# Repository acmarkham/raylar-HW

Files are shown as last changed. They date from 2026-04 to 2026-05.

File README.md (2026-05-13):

# raylar-HW
## Caracal Raylar Hardware Repo

This is the main repository for the bioacoustic platform Caracal Raylar. This is an updated version of the CARACAL EVO (2021) design, which itself is an evolution of SHUMBA (2019). The main features are:

- Six onboard microphones, low frequency rolloff 7Hz
- microSD card for storage
- Onboard GPS for precision timestamping and location
- Onboard dual band wireless (sub-GHz plus 2.4GHz) for mesh networking
- STM32U5 core, supports up to 3.5MB RAM depending on variant
- Multi-source power tree including
  - USB
  - Solar
  - Rechargeable single cell lipo
  - External battery 6V-12V
- Onboard accelerometer and magnetometer/compass for tilt and direction
- Extension connectors: 
  - QWIIC x 2 (easy to plug in peripherals like a OLED display) 
  - Mikrobus MBUS (supports a huge ecosystem of sensors)
  - EXT
  - DEBUG
- Beeper/LEDs for user feedback (errors, status etc)

## PCB

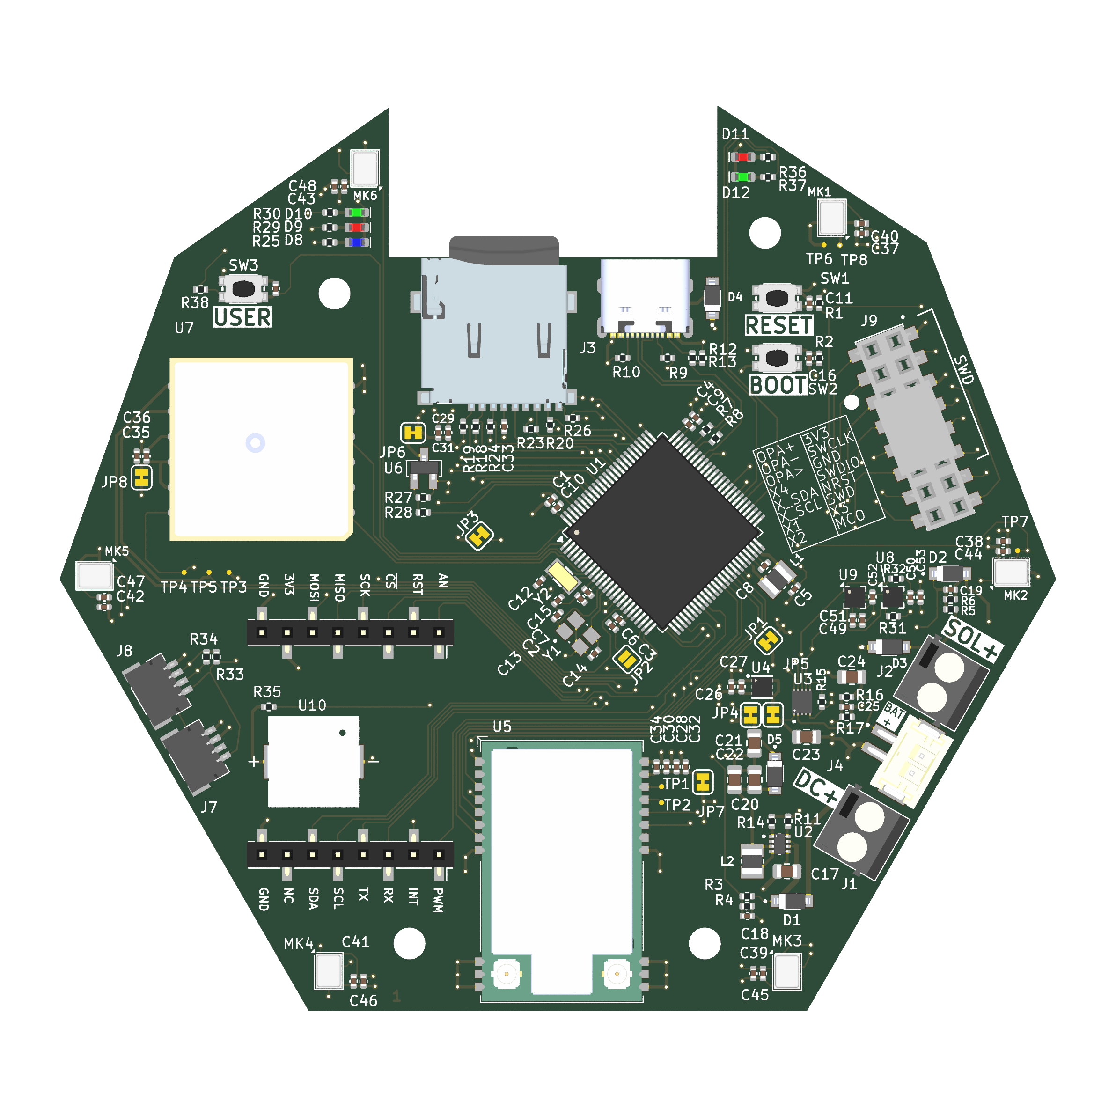
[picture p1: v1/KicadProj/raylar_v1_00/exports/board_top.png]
Top


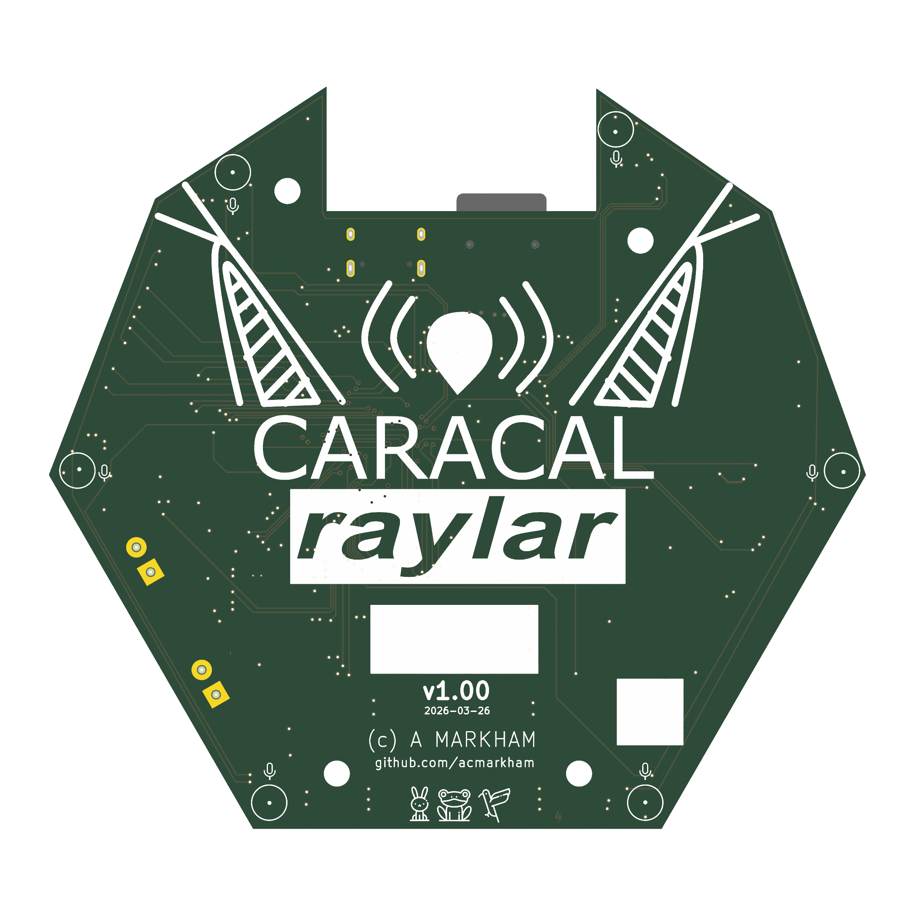
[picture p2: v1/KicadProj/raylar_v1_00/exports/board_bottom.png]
Bottom


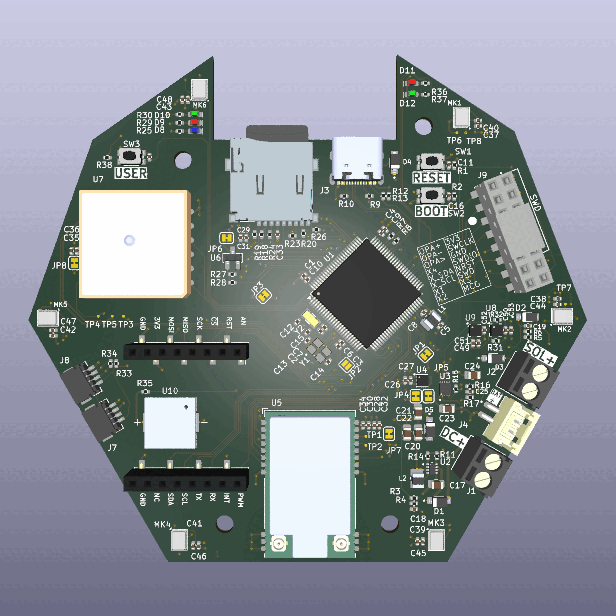
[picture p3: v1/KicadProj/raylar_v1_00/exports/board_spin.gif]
Render


## Schematic

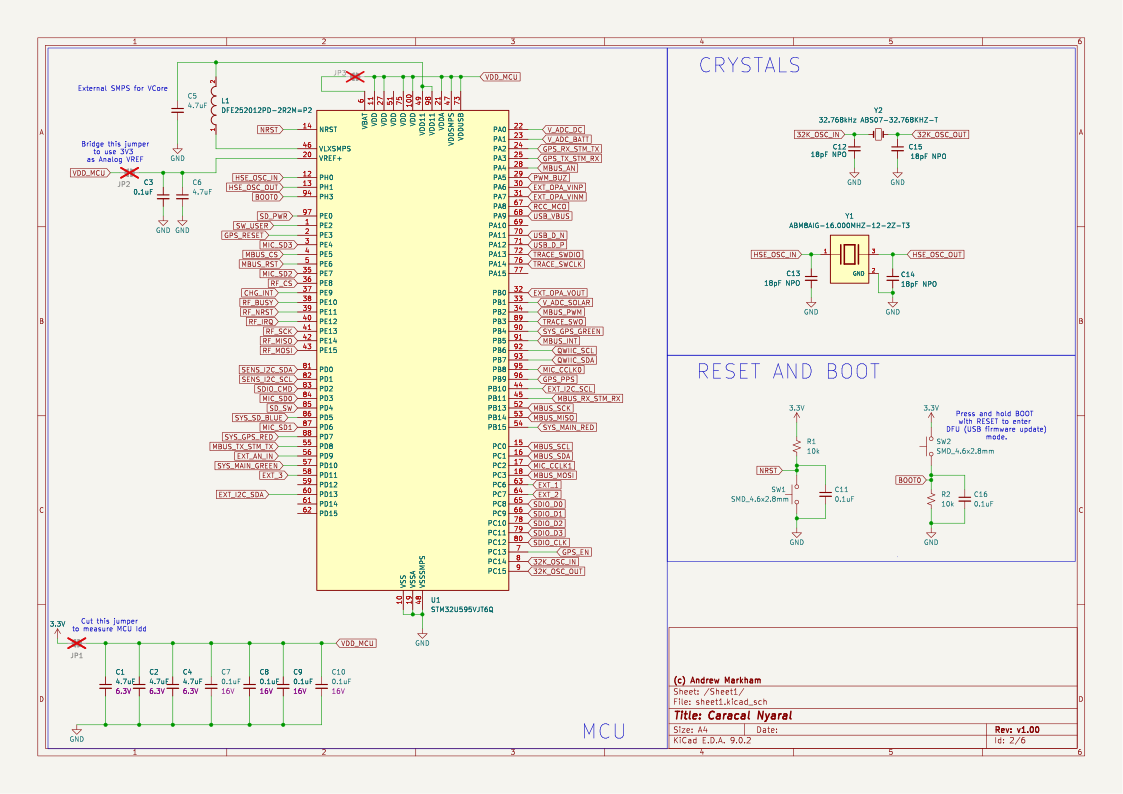
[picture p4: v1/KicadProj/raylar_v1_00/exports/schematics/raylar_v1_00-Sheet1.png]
Sheet 1 Schematic


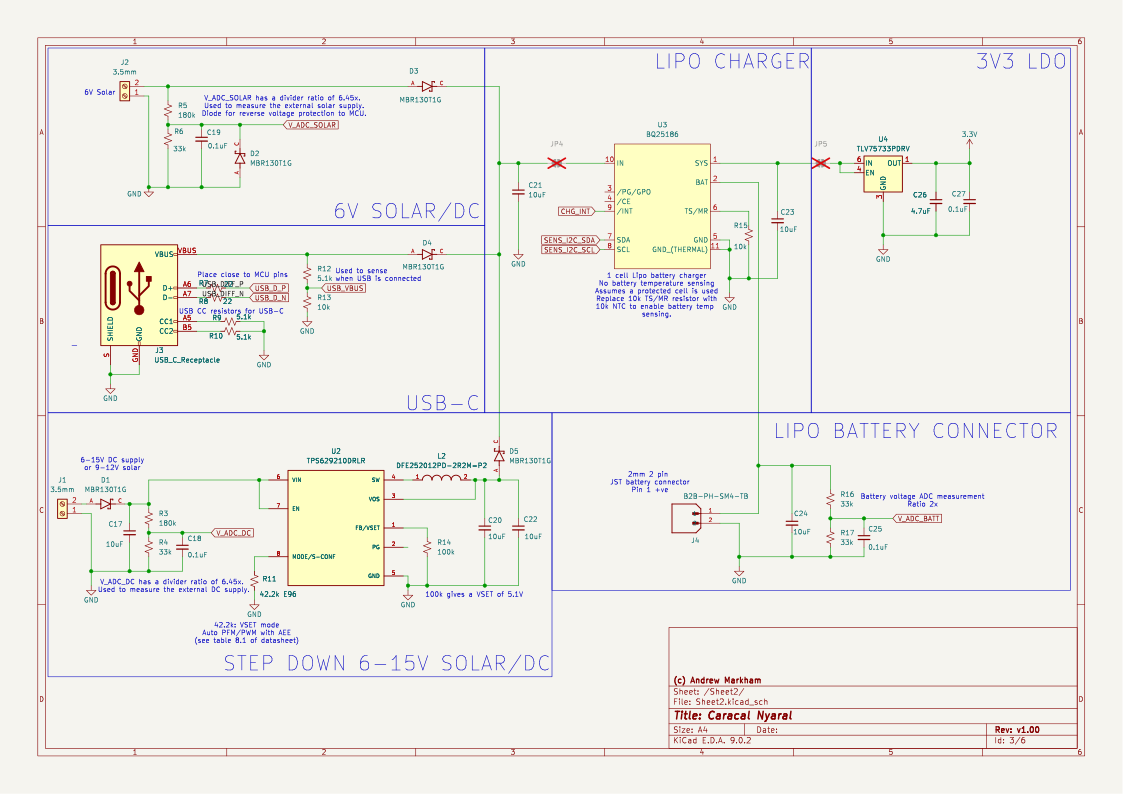
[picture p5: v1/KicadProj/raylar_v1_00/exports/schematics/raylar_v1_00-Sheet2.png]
Sheet 2 Schematic


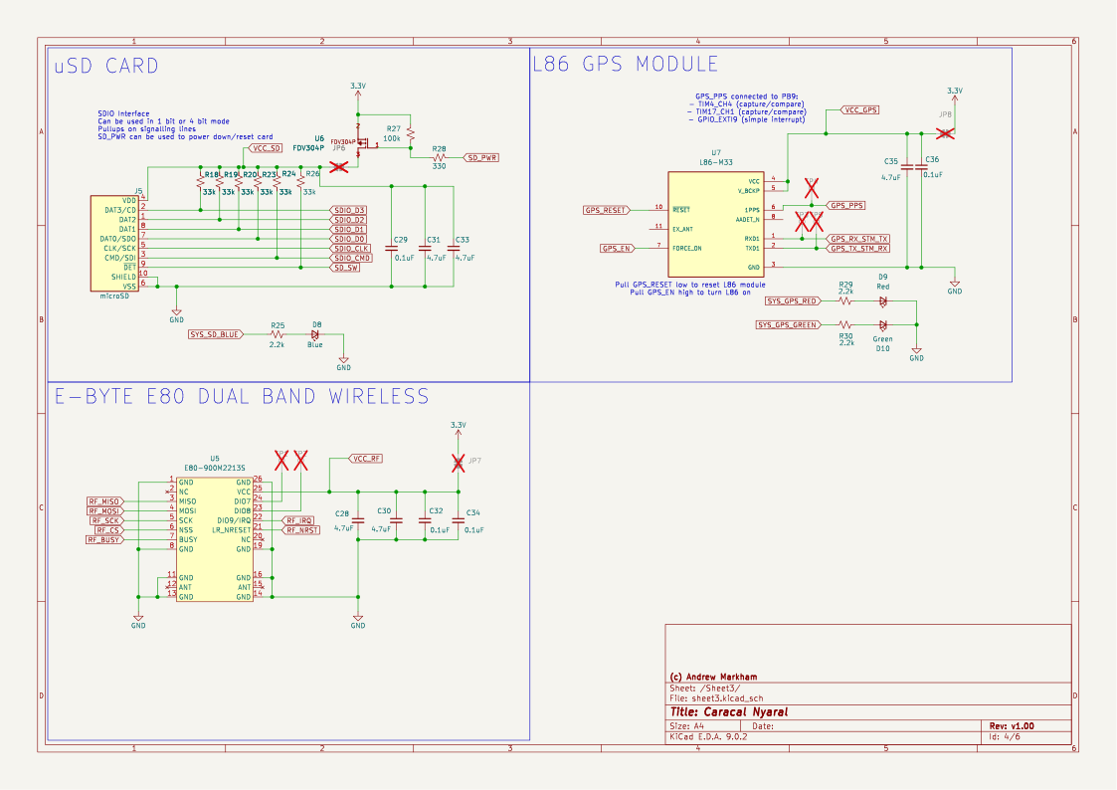
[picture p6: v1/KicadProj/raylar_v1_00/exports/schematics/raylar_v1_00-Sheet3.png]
Sheet 3 Schematic


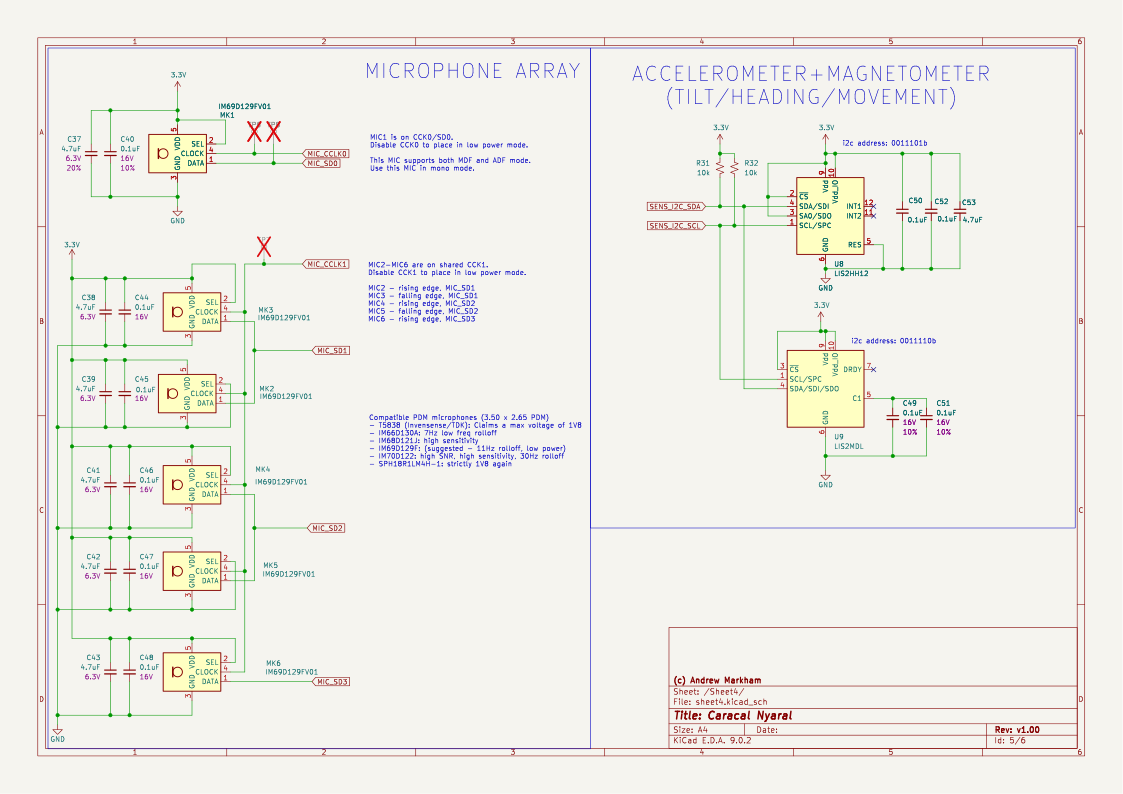
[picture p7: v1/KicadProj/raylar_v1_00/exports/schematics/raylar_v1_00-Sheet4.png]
Sheet 4 Schematic


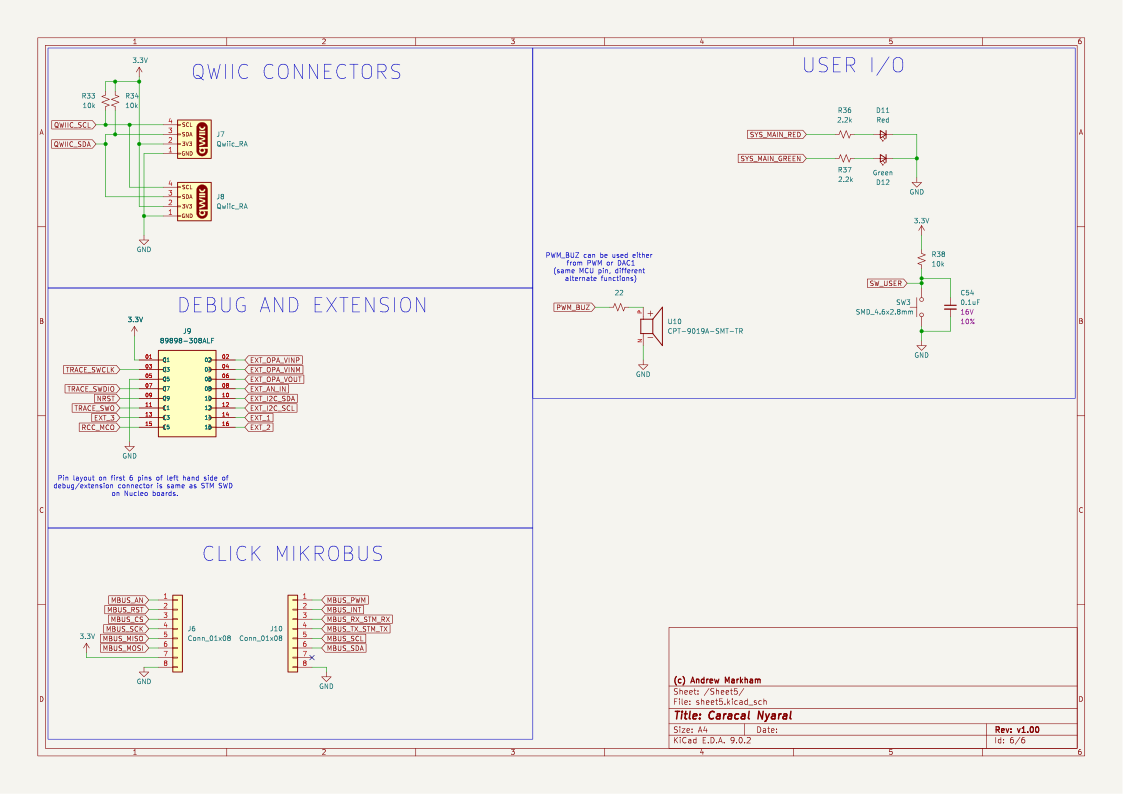
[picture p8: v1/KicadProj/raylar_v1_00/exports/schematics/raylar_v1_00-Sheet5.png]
Sheet 5 Schematic


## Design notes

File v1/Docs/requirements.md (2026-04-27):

# Caracal Raylar (formerly Nyaral) HW v1 Spec&Design

The previous variant of Caracal (Caracal EVO) had a number of features, specifically:

- 4-8 microphones, allowing for beamforming, DoA and stacking. Only 4 can be used at once because there are 4 DFDSM filters.
- GPS time synchronization, allowing TDOA and file timestamping
- SD card for long term storage
- STM32L4 micro (192kB RAM) which gave enough space for buffering
- Basic real-time processing (simple 1K NN, GCC-PHAT) if needed
- Dual source power (USB or 6-12V external battery)

For this version, the main requirements are:

* 6 microphones that can be used simultaneously (6 MDF filters)
* Lower power - previous version used around 40mA@3V when running at full tilt which is high
* Wireless connectivity - long range like LoRA as a minimum
* Onboard GPS
* Onboard tilt/direction/movement sensing
* Easy interface to additional sensors e.g. to MikroE Click or STEMMA QT
* Solar powered natively with USB or external
* Native support for LiPo 1C battery
* Voltage/charge measurement on inputs/battery
* Similar/lower price point (~$60 in 100 QTY)

Specific Requirements

- R1: STM32U5 family support (up to 4Mb RAM).
- R2: 6 high quality PDM microphones.
- R3: Wireless Interface (mesh).
- R4: GPS module
- R5: Tilt/compass sensor
- R6: Power module (solar + LDO/buck regulator). Dual input + battery charger.
- R7: microSD
- R8: Oscillator
- R9: Debug/program
- R10: User Interface
- R11: Extendability
- R12: Mesh gateway/listener
- R13: Mechanical

## Design Choices

### R1: STM32U5 family support (up to 4Mb RAM)

To be maximally compatible between wide varieties (i.e. RAM) of STM32, we will choose 100 pin LQFP package (existing caracal is 64 pin). We don't need to finalize now, but STM32U5G7VJT6 (3MB RAM $11/100) seems like a reasonable choice. Other pin compatible variants include:

* STM32U535VET6 [274k RAM] [$4.8/100]
* STM32U575VGT6 [768k RAM] [$5.0/100]
* STM32U585VIT6 [768k RAM] [$5.9/100]
* STM32U595VIT6 [2514k RAM] [$9.5/100]
* STM32U599VJT6 [2514K RAM] [$9.3/100]
* STM32U5A5VJT6 [2514K RAM] [$9.6/100]
* STM32U5A9VJT6 [2514K RAM] [$10.3/100]
* STM32U5F7VJT6 [3024K RAM] [$11.5/100]
* STM32U5F9VJT6 [3024K RAM] [$10.8/100]
* STM32U5G7VJT6 [3024K RAM] [$11.0/100]

This gives us a very neat upgrade/downgrade path e.g. to make a minimal caracal by stripping out more advanced features we can go for U575 and shave ~$5 off total BOM. For now, lets design for the max. There is also a question of package:

64 pin LQFP (previous caracal)

100 pin LQFP (reasonable "upgrade" path)

144 pin LQFP (might be a bit much, we don't have a screen or anything else that needs such a lot of GPIO)

144 pin UFBGA (could make design more complex, definitely need more than a double sided board).

Some of the smaller memory variants have 64 pin QFN which might be an option but not for the G7.

Note that there is also a -Q suffix which has a built in SMPS for the core. This can almost halve active power consumption e.g. at 160MHz run rate. It does sacrifice ~3 pins and potentially adds hash noise. But it is software enabled, so we can choose whether or not to use it in deployment.

> Choice: STM32U5G7VJT6Q (100 pin LQFP). This seems to be well supported for up/downgrade pathway.
>
> Alternatives: STM32U595VJT6Q (2.5M RAM, more widely available)

### R2: 6 high quality PDM microphones.

There are lots of variants here, we are looking for very high dynamic range and sensitivity, as well as a low frequency roll-off that will allow better infrasound. These are bottom port PDM microphones.

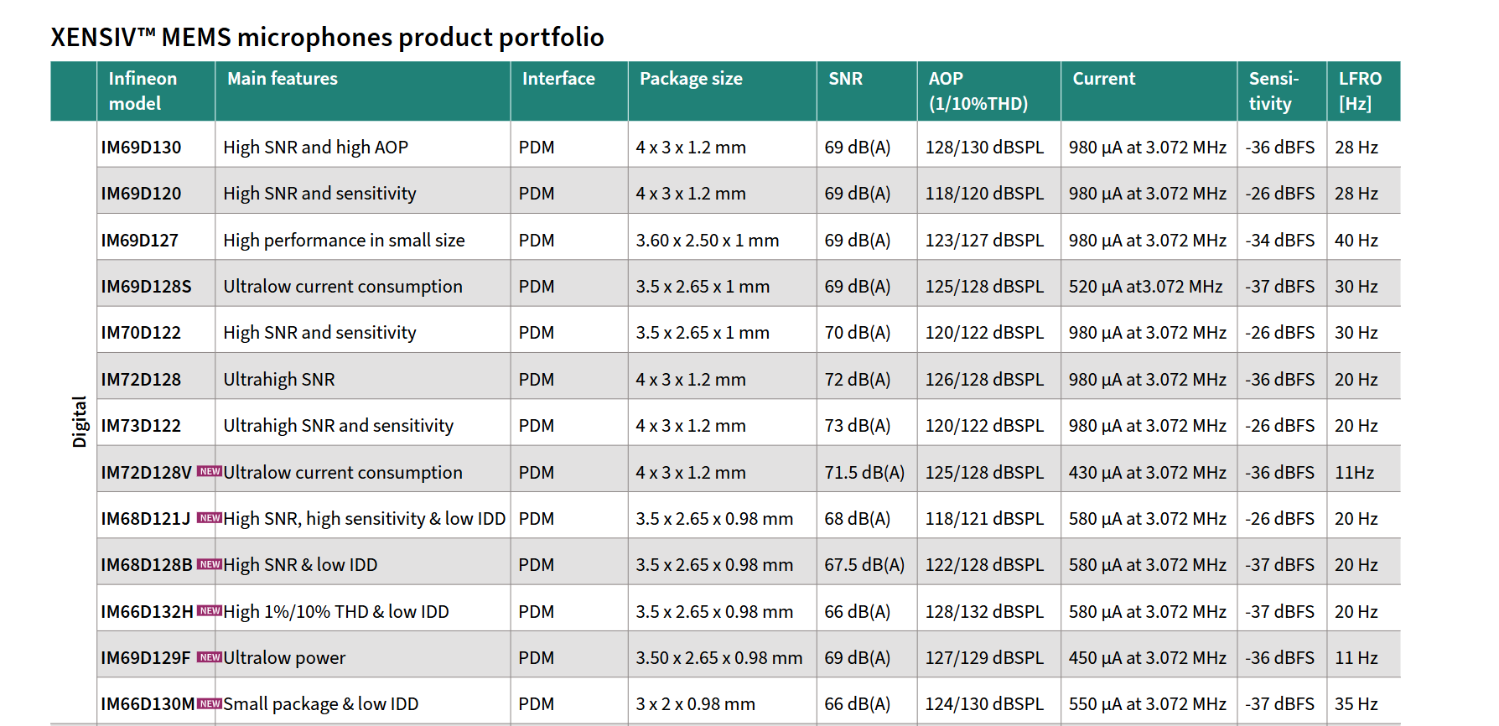
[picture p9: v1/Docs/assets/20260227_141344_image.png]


Pin compatible options include:

IM69D129F (infineon):

129dB SPL AoP, Sensitivity: -36dBFS, SNR: 69dB(A)

450uA, 11Hz LFRO.

Also, is IP57 rated which is a great feature.

3.50 x 2.65

T5838 (Invensense/TDK) [As used in the previous, second iteration of Caracal. Interestingly, it claims max supply voltage is 1V8, so it must have been unhappy).

133dB SPL AoP, Sensitivity: -41dBFS, SNR: 68dB(A)

310/120uA, 27HZ LFRO

3.50 x 2.65

Strictly, 1.8V max, which could be problematic

Others include Syntiant(Knowles)SPH18R1LM4H-1 [30Hz rolloff, 68dB(A)], (Infineon)IM66D130A [7Hz(!) rolloff, 66dB(A), 130dB AOP, 1100uA]

In a larger package (4x3) we have:

IM72D128V which has 71dB SNR.

> Choice: IM69D129FV01 (might be tricky to obtain as it is relatively new). Footprint is standard however, so many pin compatible options exist.

### R3: Wireless Interface (mesh)

This is challenging, as we want everything without having to pay for it ($BOM, footprint, power, opex). The base is LORA - this will allow easy compatibility and it is field proven to be long range. The next dimension to consider is DIY RF or solder down a module. Modules are more expensive, but are FCC/CA tested, so it reduces risk and does not need its own certification. They also are much lower risk in terms of impedance matching, board layout etc.

Main chipsets are SemTech and HopeRF.

SemTech LR1121 and LR2021 are dual band, which allows dense plus long-range meshing.

* Ebyte E80-900M2213S is LR1121 based ~ £5.80. Package is quite consistent across Ebyte modules. Widely available (even on Amazon). 26x16mm. Dual band. Antenna connector on module. Even supports L-band satellite uplink.
* Seeed studio Lora-E5-HF - based on STM32WLE5JCSTM3. Single band.
* RAK3172: Lora-E5-HF. Single band.
* Murata: LBAA0XV2GT-001 LR1121 based. ~£12.00. Dual band. Antennas are external traces, not on board, so that is a faff. But very small: 9.98 × 8.70mm. And probably more robustly designed than ebyte. Available at digikey. Compatible with different murata module, but will require different matching/front-ends.
* Core1121 (waveshare) ~$10ea. compatible with lots of different waveshares.
* Seeed Wio-LR1121 (IPEX4 1.5mm onboard). Does not seem to be available.
* LoRa1121 (NiceRF). Not neccesarily widely stocked/available.
* EMB-LR1121-e (Embit): EU company, no visible pricing

> Choice: EByte E80. But pull out the same pins for interfacing to a different module if needed. Consider dual footprint for alternative e.g. core1121 or RAK series as well to be safe?

### R4: GPS module

We have used ublox el-cheapos to date with varied results. Options are:

- External GPS + Antenna (connect via cable)
- Onboard GPS + External Antenna
- Onboard GPS + Onboard Antenna

External GPS + Antenna is the most flexible as we can chop and change antennas easily. But it is a nuisance because soldering is required by an end-user to add on the GPS. For 100 boards, this can easily take hours of time. I think we can safely discount this as a main option, but can easily have the GPS pins (power, serial RX/TX, EN, PPS) broken out anyway.

Onboard GPS + External antenna makes board config not a big issue as it doesn't really matter where the GPS is in terms of sky view/blocking. It also makes it simple to re-orient the board (horizontal/vertical) without heavily impacting skyview. It can be a risk in terms of antenna cables flapping around and falling off. This will be an issue anyway for the RF block, so it possibly is not a massive issue.

Combined GPS + antenna is super nice from a design perspective because a single "lump" just works.

- SAM-M8Q: (fully onboard). ublox GPS M8. Lovely, but expensive at ~$20/100
- SAM-M10Q: (fully onboard). ublox GPS M10. Amazing, but more expensive at $22/100
- Quectel LC86G: fully onboard. $8/100. Footprint compatible with L80 and L86 module.
- Quectel LC86L: fully onboard: £7/100. Compatible with Quectel GPS module L80.
- DAN-F10N-OOB: fully onboard. $15/100. dual band. ublox.

External antenna:

* max-f10s-oob: external antenna. $15/100.
* TESEO-LIV3 series 18LCC ~$10/100

External antenna options will be painful as they will need proper board routing. My bet is to go for Quectel series and then provide another GPS breakout to give max flexibility.

> Quectel LC86L. Secondary breakout for external GPS.

### R5: Tilt/compass sensor

Currently the device has to be manually surveyed in place which is painful. This is to ensure that MIC1 is facing north. An easier way is for the board to just "know" which direction it is facing. Conceptually easy, but compasses can have major hard-iron issues. Nonetheless, it should be better than the current approach. Adding a tilt sensor (accelerometer) will also allow for sensor to be placed at arbitrary tilts and then this info used. Tilt sensor can also be used for wakeup/theft/tampering detection.

* Bosch BNO055. 9 axis IMU. $9/100
* LIS2HH12TR (acc) + LIS2MDLTR (mag) - $0.6 + $1
* LIS3DHTR (acc) + LIS2MDLTR (mag) - $0.8 + $1
* Melexis: MLX90392ELQ-AAA-010-RE (mag) - $0.51
* LSM303AGR: eCompass - $2.55/ea (long lead times)
* ICM-20948: Full 9 axis IMU - $5

> Choice: LIS2HH12 (acc) + LIS2MDL (mag)

### R6: Power module (solar + LDO/buck regulator). Tri input + battery charger.

Here, we want to be able to flexibly power our modules from:

- A standard 1 cell rechargeable lipo (3v6), charged by USB/Solar
- USB
- Solar
- External VBAT (6-12V)

### Charger options

* bq25185: Very simple, minimal BOM $1.2/100. Diode OR for the multiple power sources. Also, without the battery, it just does a straight pass-through, so the battery is actually optional.
* BQ25186: Same as bq25185 but with i2c i/o. Newer, so might be harder to get hold of.
* bq24074: higher charge current, supports higher voltage panels $1.3/100
* BQ25895: i2c telemetry and control $2/100
* LT3652: MPTT $5/100

### 12V buck options

For a higher voltage input, we don't want a linear regulator as it will drop the excess voltage as heat. Instead, we use a buck which is more efficient.

TI **TPS62160** (3–17 V in, 1 A sync buck, high switching frequency)

TPS629210 (3-V to 17-V, 1-A, high-efficiency, low-IQ, synchronous buck converter in SOT-583 package)

### Fuel gauge:

* BQ27441 (and -G1 suffix): colomb counter $1.8/100
* BQ27532
* MAX17048: voltage shunt $2.2/100

### Voltage regulation

* We need to drop the SYS regulated voltage down to stable 3V3 (or perhaps lower? It is probably now only the microSD that wants a higher voltage...)
* We can buck-boost, boost-ldo or just LDO. LDO looks like the most straightforward...
* TPS72633
* MCP1700 series (170mV drop at 250mA), $0.4/100. Iq is 10uA
* MCP1824 series (300mA), $0.5/100. Iq is higher at 29uA typ.
* TLV75733: Full part number TLV75733PDRVR (1A), Iq is 25uA typ

https://e2e.ti.com/support/power-management-group/power-management/f/power-management-forum/1605244/bq25185-bq25185---simple-solar-charging-circuit?tisearch=e2e-sitesearch&keymatch=bq25185#:

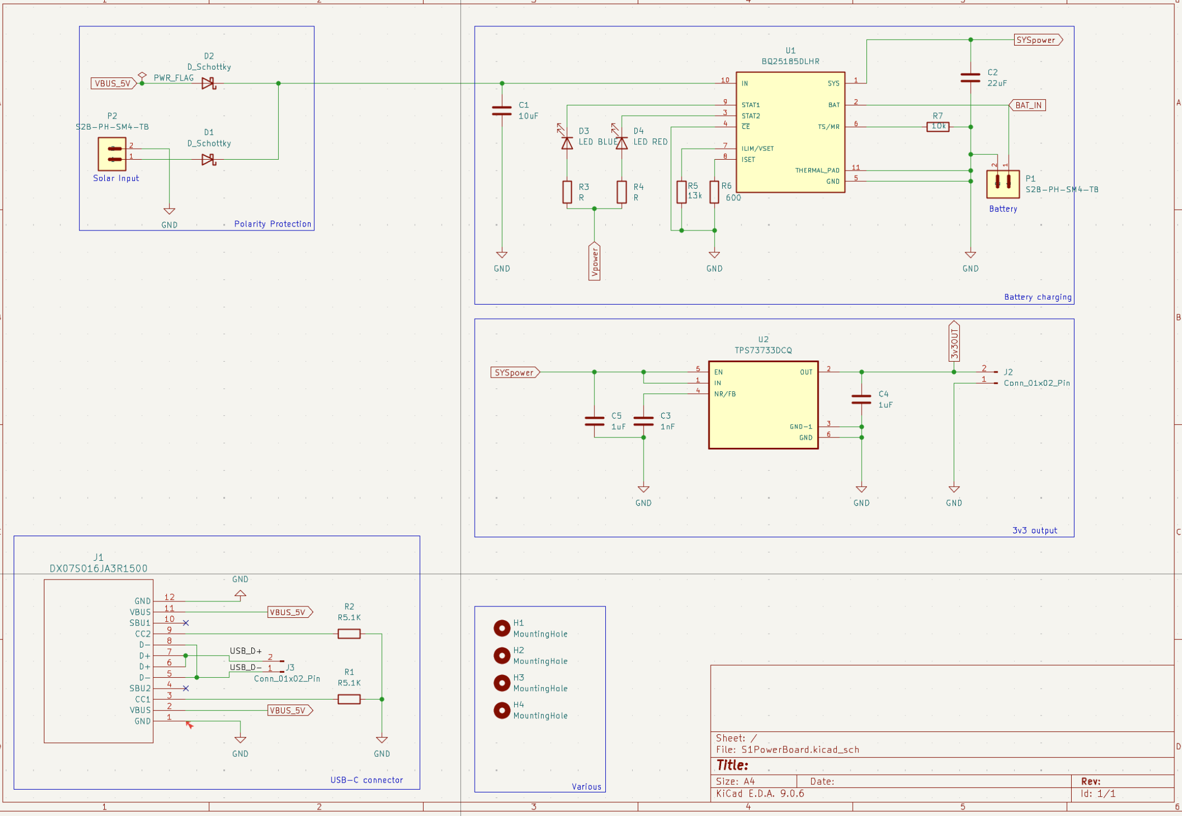
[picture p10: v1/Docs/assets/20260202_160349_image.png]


> Choice:
>
>> BQ25186 for battery charge and passthrough
>>
>
>> TPS629210 buck from external 6-12V down to 5V
>>
>
>> BQ27441 (optional) for colomb counting, can use MCU ADC for very rough estimate.
>>
>
>> MCP1824T-ADJE/OT for adjustable, stable 3V rail
>>

### R7: Microsd

We want to be able to use microsd in SDIO mode, but also to power it down. This is necessary for low power consumption and also sometimes needed for reset.

- Use 10k pullup on signalling lines (some use 33k or 47k)
- Use 22R to prevent high speed ringing (optional)
- 10uF X5R decoupling (at least)

Here is an example of low voltage (1v8) SDIO:

https://oshwlab.com/grafalex/low-voltage-sdio

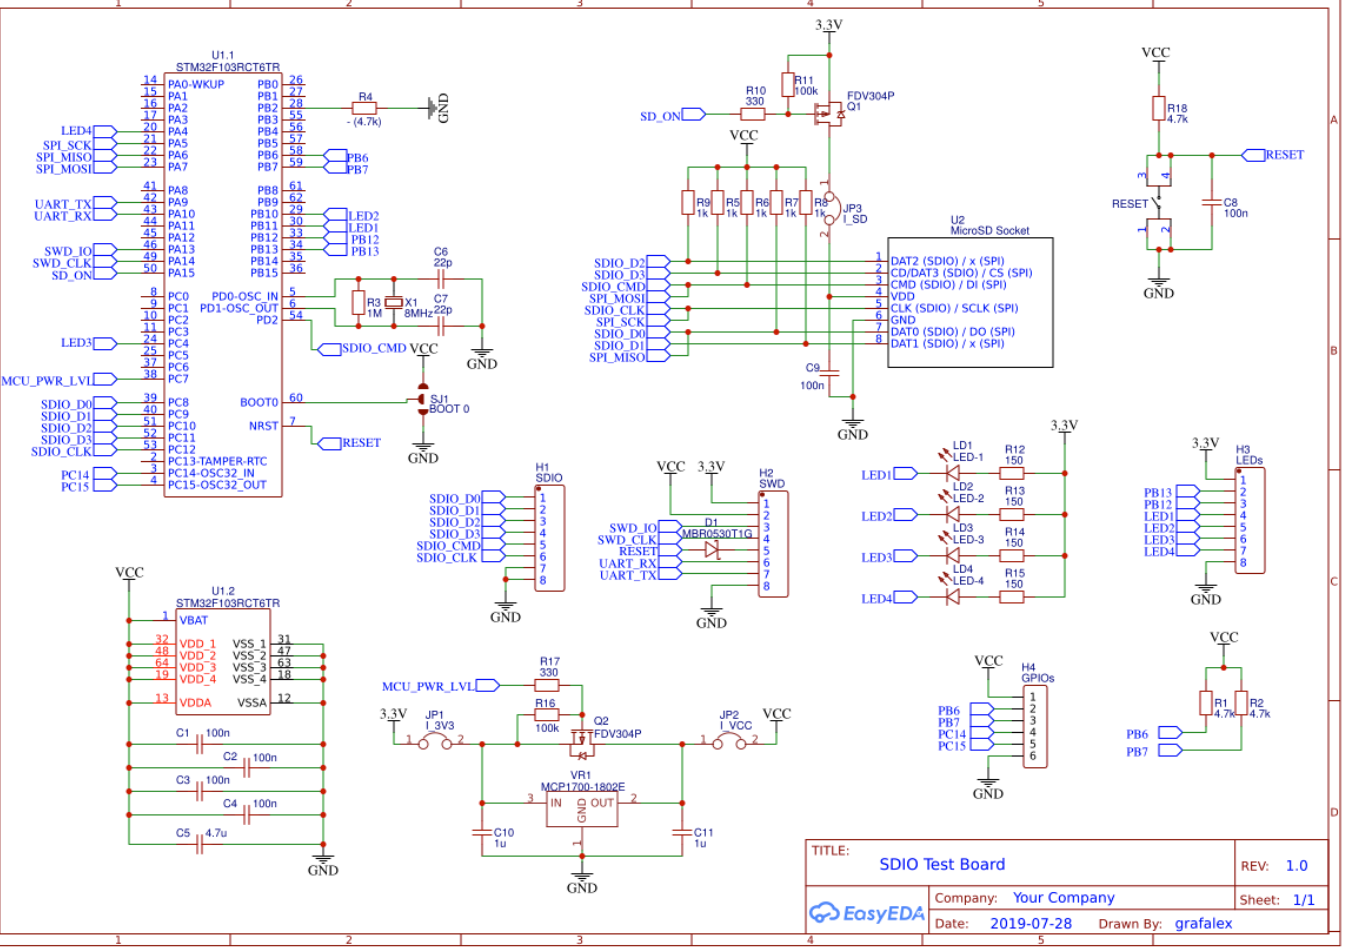
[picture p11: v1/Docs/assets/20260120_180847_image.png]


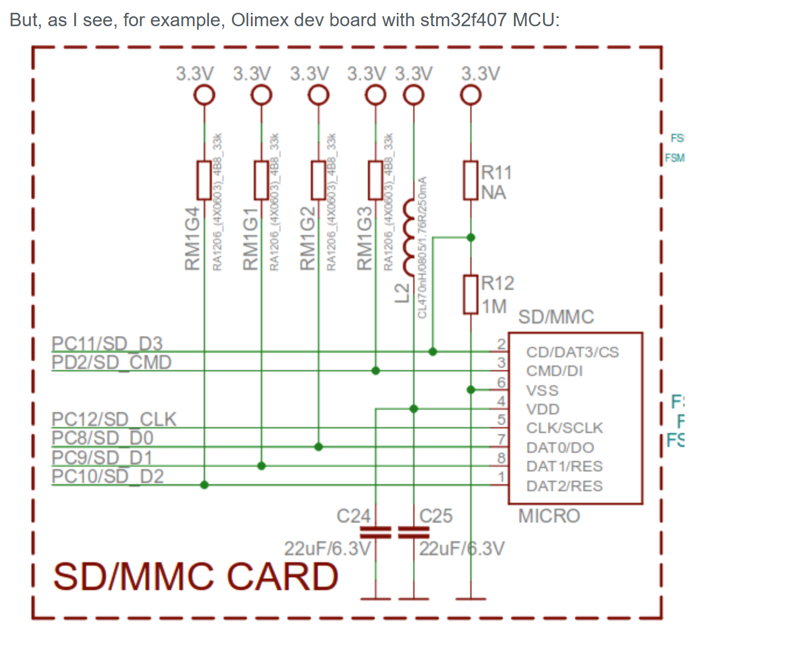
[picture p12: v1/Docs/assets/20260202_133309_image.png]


For power control:

- TPS22917: high side power control with inrush ($0.6/100)
- FDV304P: P-channel mosfet ($0.12/100)

> Choice: TPS22917. 10k pullups. No 22R ringing resistor. SD card presence switch. 10uF/100nF X5R decoupling. Push-push SD card.

### R8: Oscillator

We need a reasonable XO for HSE. In particular, for Caracal EVO, small drifts lead to files not having a "true" sampling rate e.g. of 16kHz. This especially will become more pronounced towards the end of the file as the epoch is synchronized at the beginning. This can lead to tens of milliseconds of sampling offset with a standard 20ppm XO. Although we use GPS to start each file on the top of the hour, we don't modify the actual sampling rate. STM32U5 has a nice feature (fractional PLL) which can provide finer grained frequency stepping. We can use GPS PPS to make a GPS disciplined oscillator to get below 1ppm sampling rate error.

* Abracon ASEMB-16.000MHZ-LY-T: Oscillator MEMS 16MHz ±10ppm (Stability) 15pF LVCMOS. $0.9/100. 10mA(!) current consumption.
* ABRACON ATX-H11-F-16.000MHz-G100-T: 10ppm MEMS, $1/100. 4.8mA current consumption
* SiT3907AC-2F-33NE-16.000000Y: 10ppm MEMS, limited supply, $8/100
* ABM10N-16.0000MHZ-8-D1X-T3: 10ppm XO, $0.5/100. Tiny package SMD4
* ABM8AIG-16.000MHZ-12-2Z-T3: 20ppm XO, $0.7/100. 3.2x2.5 standard package.

Do we need a 32kHz oscillator? These can allow for backup time/date without running HSE. I am not convinced this is necessary as power budget is largely dominated by RF and GPS, not so much idle. Also, when running PDM, it is most likely we will be clocked from HSE as we need PLL for MCO.

> Choice: ABM10 or ABM11 series if footprint works. ABM8 for more flexible variant.
>
> ~Choice: No 32kHz in this iteration~
> Actually, lets go for a 32kHz, AB07 series

### R9: Debug and program

For debug, the main options are to consider which connectors to use onboard. The simplest and cheapest is to just have solder/test pads and use a small set of boards as designated debug boards. This is simple, but can be a little limiting if a broken board (in the field) does not have a connector. That said, it is unlikely that board-specific debugging would be done anyway. Another option is to use pogo pins/test connectors like `Tag-Connect (TC2030 / TC2050) 6-pin footprint (no header or legs options)`. There is zero board cost as it is just a cluster of pcb through holes, but the connectors can be expensive. This can make it hard for others to use directly. Again, it is not clear how many "others" will be doing debug... Last option is to use a cortex debug connector, typically a 0.05" pitch SAMTECH 2x5 pin header. This is easy to use and widely compatible. Board costs do rise by ~$1 in small quantity for the header. Part number Samtec FTSH-105-01-F-DV-K or cheaper (FTSH-105-01-L-DV-K) is good as it has the shroud around the pin headers so they are less likely to get bent/damaged (which has happened to a lot of Caracal evo connectors).

For program, it can obviously be done through the debug connector. But it is much easier to support DFU over USB. This requires two pushbuttons, one for reset and the other for boot.

*Update* Drop the 10 pin cortex debug and replace with pinout on the extension connector. We can just jury rig an adaptor rather than populating all boards with this debug connector that is not really widely used.

> ~Choice: 10 pin cortex debug: FTSH-105-01-L-DV-K. Can be left unpopulated if cost is really an issue~
>
> Choice: Break out the debug connectors on a generic pin extender (see R11)
>
> 2 SMD pressbuttons for boot/reset

# R10: User "Interface"

Caracal Evo has 3 leds (red, green, blue) and a buzzer/speaker as a UI. Feedback from the field is that the buzzer is actually super useful as you don't need to watch flashing lights, you can just listen to tell if it is happy or not. There is a question as to whether *more* UI is required and what that would look like.

* Use a display. OLEDs are relatively inexpensive ($10) but would bump up the BOM quite a lot. Standard approach is something like SSD1306 OLED via I2C.
* USB CLI + Minimal Local UI - using USB-C, this can even talk to mobile phones, so they can be quite useful "displays" in the field just using a serial terminal.
* More LEDs. Adding a few more LEDs for status (e.g. GPS, RF) wouldn't hurt terribly and wouldn't bump up BOM a lot, but they can be confusing e.g. tell me what the LED in the top right corner is doing.
* Better debug with "spoken" messages/errors. We have plenty of RAM, we use PWM to make the buzzer play tones, but we could also just have recordings of errors to do robot speak. This could be irritating, but perhaps useful.
* OTA debug - if device is connected to mesh, it can send status messages.

Preference would probably be to stick with a few LEDs and use USB CLI for any richer debug. We will also get messages (hopefully) over RF mesh which can help give other high level error conditions/warnings. We can also just plug in an OLED via a QWIIC connector to get ad hoc diagnostics:

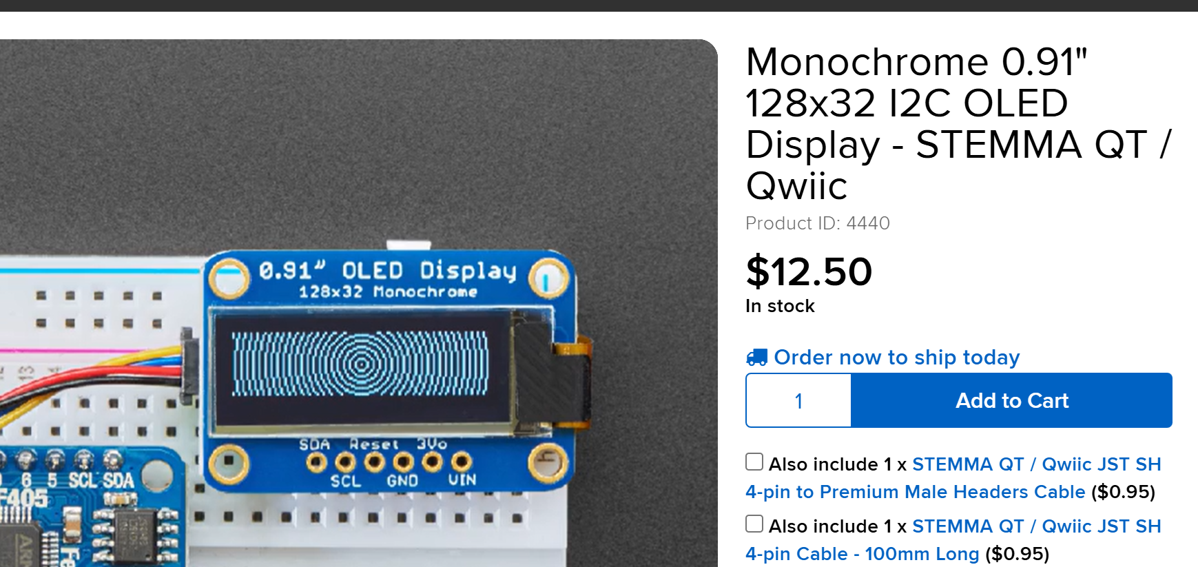
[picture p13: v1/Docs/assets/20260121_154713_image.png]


> LEDs
>
> Buzzer
>
> USB CLI (no changes needed except to connect data pins to USB on STM32U5)
>
> I2C connector for easy plug and display

### R11: Extendability

A challenge of something like this is it is hard to design something that is perfect for everything, especially future uses that might not have been considered at design time. Having an easy ability to extend/add functionality without making it a monstrosity is necessary. Caracal Evo used a single 10 pin 0.05" header. In practice, this was quite hard to solder new things on to in an ad hoc manner (it was thought that new adaptor boards would be designed but that never happened). Instead, it makes sense to try and leverage the enormous hobby market (sparkfun, adafruit, rpi and mikroE) to allow for relatively quick and easy mods. Options include:

* solder pads for breakout
* pin headers for breakout
* stemma qwiic/qt standard: 4 pin i2c breakout, board edge receptacle: JST SM04B-SRSS-TB ($0.5/100) or JST SM04B-SRSS-TB(LF)(SN) ($0.45/100). i3c is not supported by STM32U5 unfortunately (but is by U3!).
* mikrobus - two female pin sockets that break out a lot of standard pins (SPI/PWM/I2C). mikrobus is trademarked/copyrighted, so whilst a "compatible" header can be provided on the board, it can't be called click but it should be called mikrobus. Guidelines are here: [https://www.mouser.co.uk/pdfdocs/mikroElektronika_mikroBUS_specification.pdf] and here: [https://download.mikroe.com/documents/standards/mikrobus/mikrobus-standard-specification-v200.pdf].
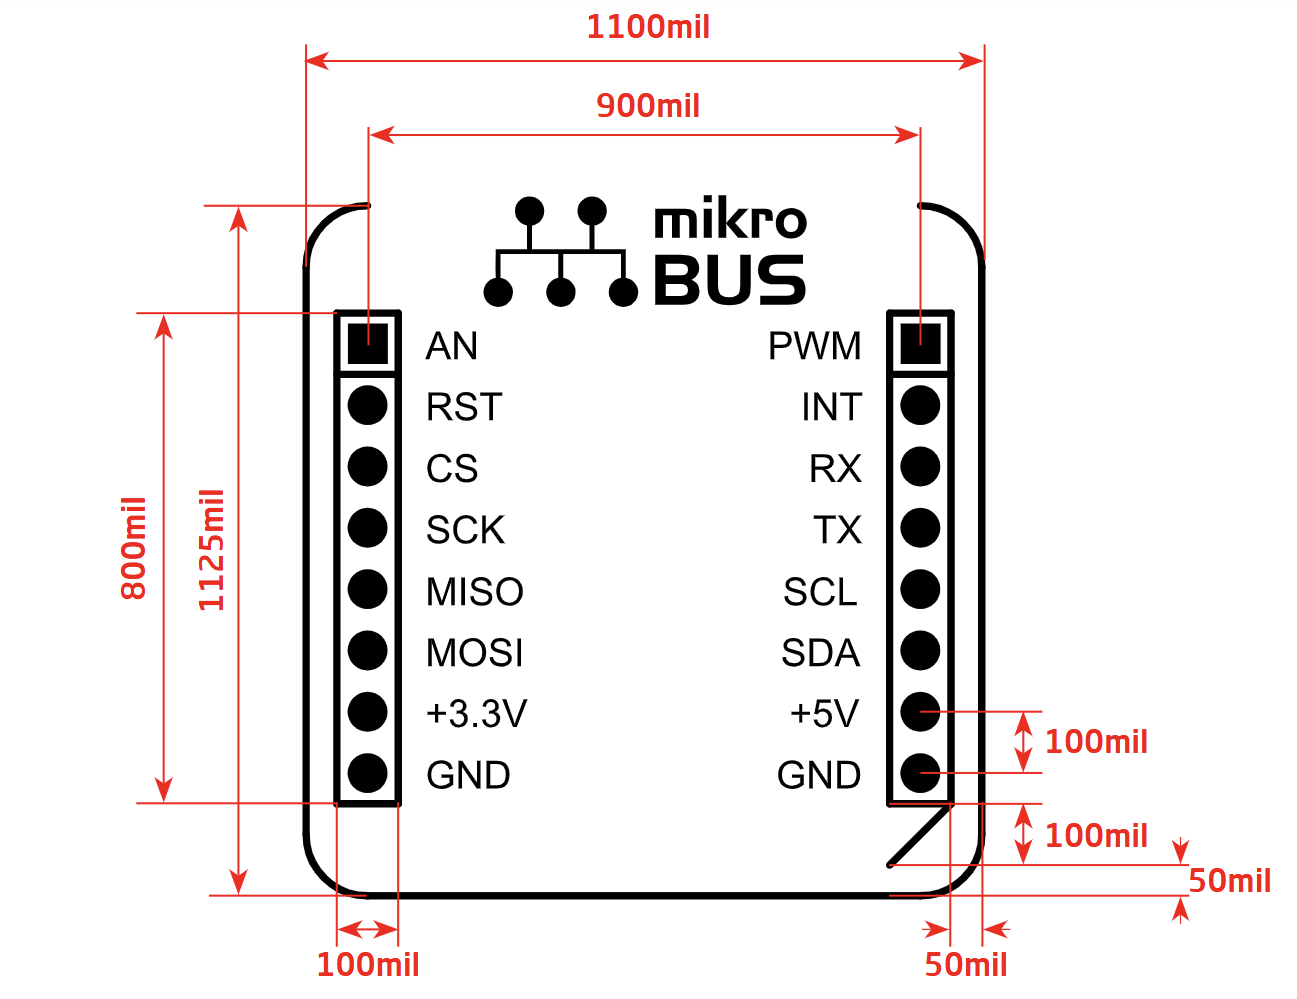
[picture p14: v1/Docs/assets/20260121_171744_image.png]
* 
* It probably makes sense to use something like the mikrobus just because it has all the useful pins anyway plus there is a massive ecosystem of compatible boards. There is also an option to use a 8x2 IDC header on board that allows for a "shuttle" board to be connected via a cable

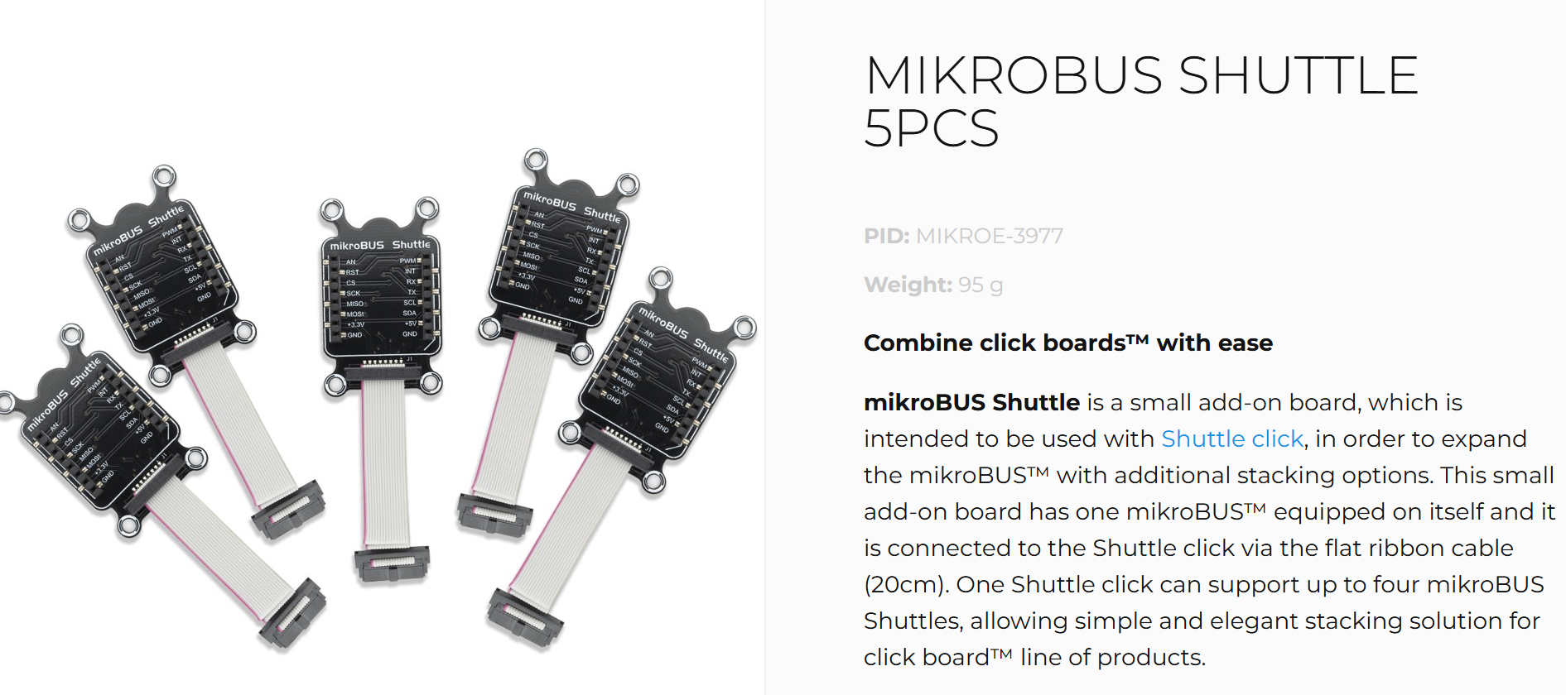
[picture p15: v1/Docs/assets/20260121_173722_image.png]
  

> Choice:
>
> 1 or 2 Qwiic connectors (up to 4 I2C in STM32U5, but one at least will be absorbed by ACC/MAG).
>
> ~~1 mikrobus (or shuttle).~~
>
> Use two 2x8 smd female headers that will support both mikrobus pinout (on the outside) and debug, breakout etc on the inside. This is a total of 32 pins, so a lot of breakout/extension.
>
> Some testpads, perhaps for any logic analyser, timing etc.

### R12: Mesh gateway/listener

To have a functional mesh, it is also necessary to have a bridge to the external world. At the simplest, this can just be a caracal nyaral device exposing data over a USB serial connection. This is most likely how it would be used in the field, which would give capabilities both as a gateway node and a listener. As a gateway, it would probably sit as an end-device next to something more substantial like a SBC/RPi with consequently larger solar etc.

> Choice: No design mods needed

#### R13: Mechanical

#### R13.1: Board shape, size and thickness

- FR4
- 1.6mm
- 1oz Cu
- ENIG surface finish (gold plated, generally quite robust and corrosion resistant)
- Overall board size depends on:
  - Dims of all modules/components with GPS/RF/MCU/SD taking the majority of board space.
  - Caracal EVO is 86mm dia circle with mics on 80mm dia circle. This is a comfortable board size.
  - We have had good experience with DIY enclosures made from 110mm  (outer) dia waste pipe vents/caps. These have an inner diameter of around 103mm. So 100mm seems reasonable.
  - We could probably make a larger board iff there is still space for access and cabling
  - A 2-3cm clearance for microSD and usb is probably sufficient. We don't have to have a uniform/symmetric board and can make a wacky shape very easily.

#### R13.2: USB and microSD

- current approach is board edge i.e. horizontal. This can be a pain to get cards in and out of a tight enclosure, but it is mechanically strong and simple.
- alternative could be right-angled connector or a true vertical connector. These might require like a 3D printed support/chimney to make them more robust.

  * vertical USB: Amphenol FCI 10132328-10001LF ($2/100). Perpendicular to board, but probably would need mechanical stiffening to be safe.
  * microSD vertical: PJS008U-3000-0 (£1.1/100),
- Another alternative is a daughterboard (either flex cable or rigidly attached to main board) e.g.
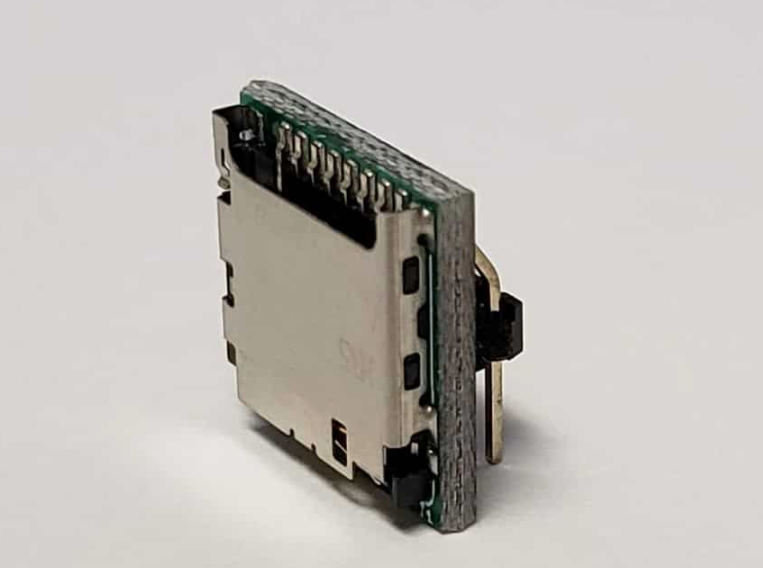
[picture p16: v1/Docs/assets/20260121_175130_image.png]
- 
- Further alternative is to cutout board to give a little more space for these.

> Choice: Use regular side entry USB and microSD (push-push). Consider board cutout to give a little more clearance. Might not be a big deal e.g. with a hexagonal board.

# Design and Layout

1. Use sparkfun kicad libraries through plugin manager to get good footprints for the standard things like usb/micro-sd
2. Use snapeda for other components, esp for 3D step models
3. ebyte e80, use this kicad model: https://github.com/KunYi/EBYTE_E80_DEMO as a footprint and 3D. We still have to make the symbol.

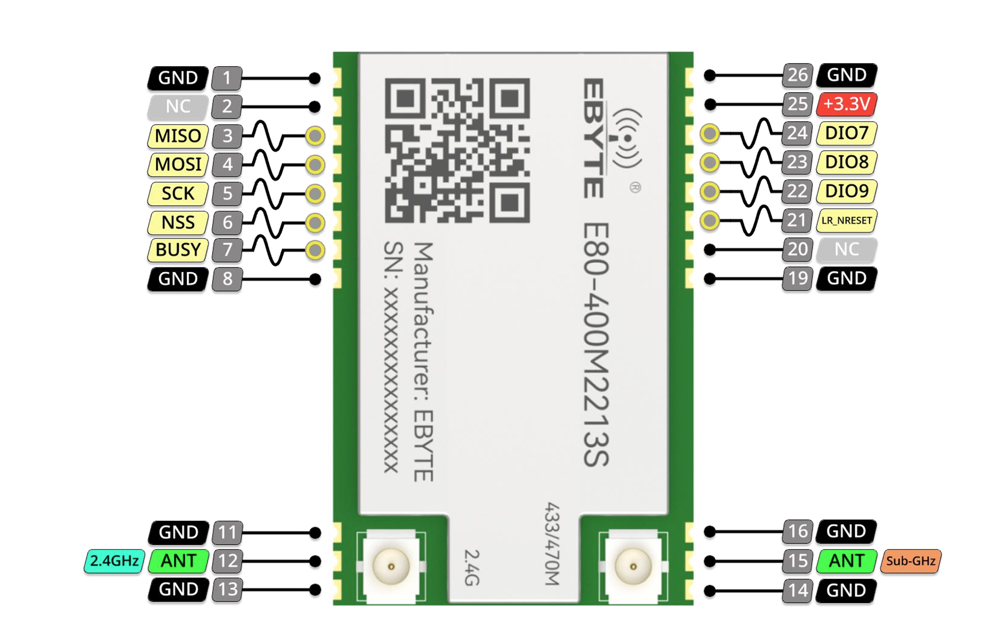
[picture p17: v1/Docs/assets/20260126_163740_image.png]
   

   There is some other important info about connections viz:
   DIO9 is actually IRQ
   DIO5/6 control RF power:

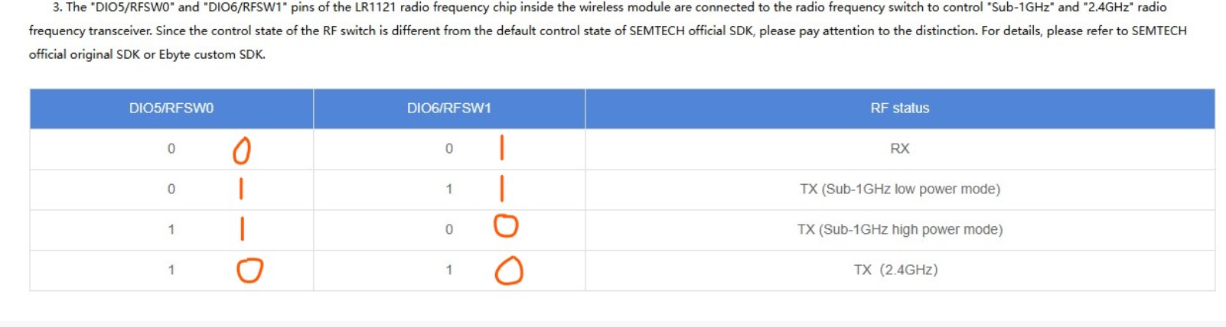
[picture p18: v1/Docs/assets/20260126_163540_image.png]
   

   https://github.com/jgromes/RadioLib/discussions/1386

   Suggested circuit diagram from the manual:

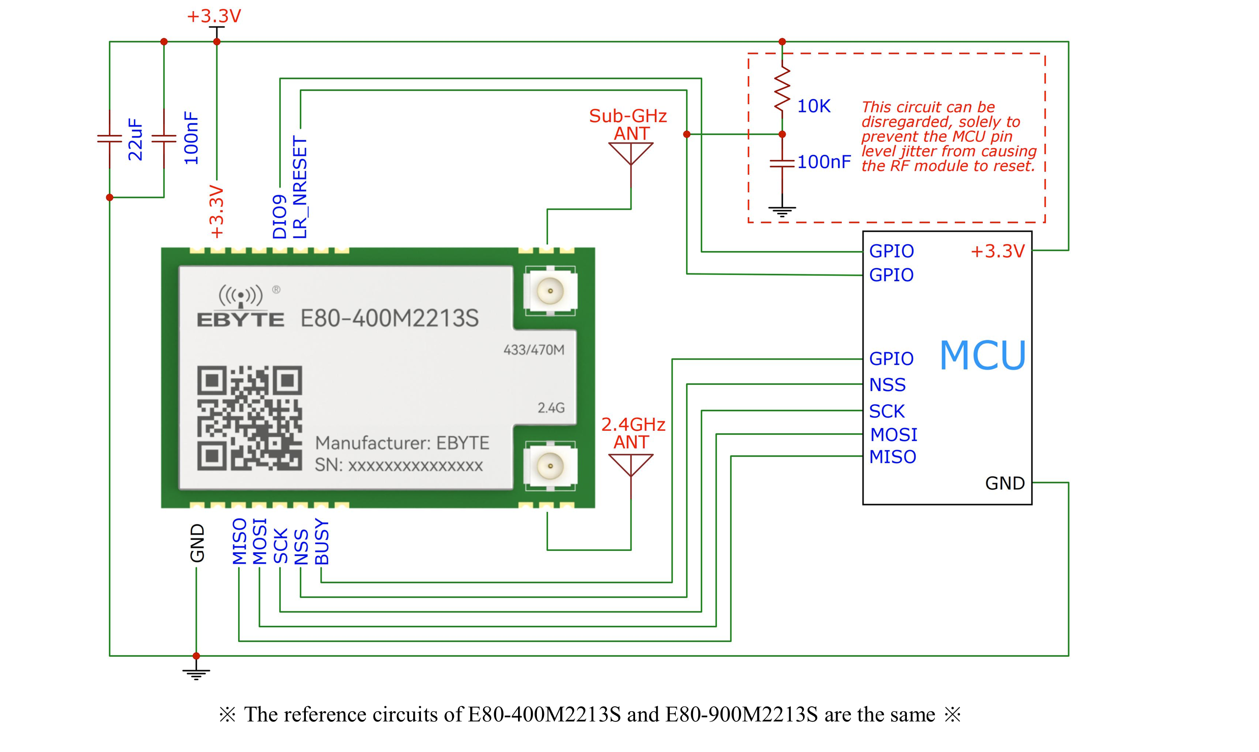
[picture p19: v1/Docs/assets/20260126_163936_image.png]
   

There is something potentially dangerous that is reported on the ebyte80 github in that:

`**Important Note:** The dimensions between pin8/pin11 and pin16/pin19 are shown as 11.17mm in the official STEP model, which differs from the 11.20mm specified in the user manual. Please verify these measurements with your actual module before designing your PCB, as I haven't physically measured the module myself.`

The difference is probably small enough (0.03mm) to be within tolerance (claimed to be 0.01mm). 30 micron is ~1.1mil, track width is 6/6. We can potentially try and measure an actual unit, but I think we aren't going to easily see this offset. For now, the footprint simply matches up with the official step model i.e. we are using 11.17mm as the spacing.

### S6: Power supply implementation

There are quite a few things to think about here.

#### S6.1: 12V buck

Nominally, we would like to support plugging in a car battery or similar without things exploding. Rather than dropping this across a linear regulator, which would be quite a big drop (and hence the dropped voltage just turns into heat), we instead drop the main voltage down to ~5V so that it can sit alongside the 5V USB rail. We use a TPS629210 buck which goes up to 17V/1A which is pretty substantial.

To program the output voltage, table 8.2 in the datasheet has the VSET:

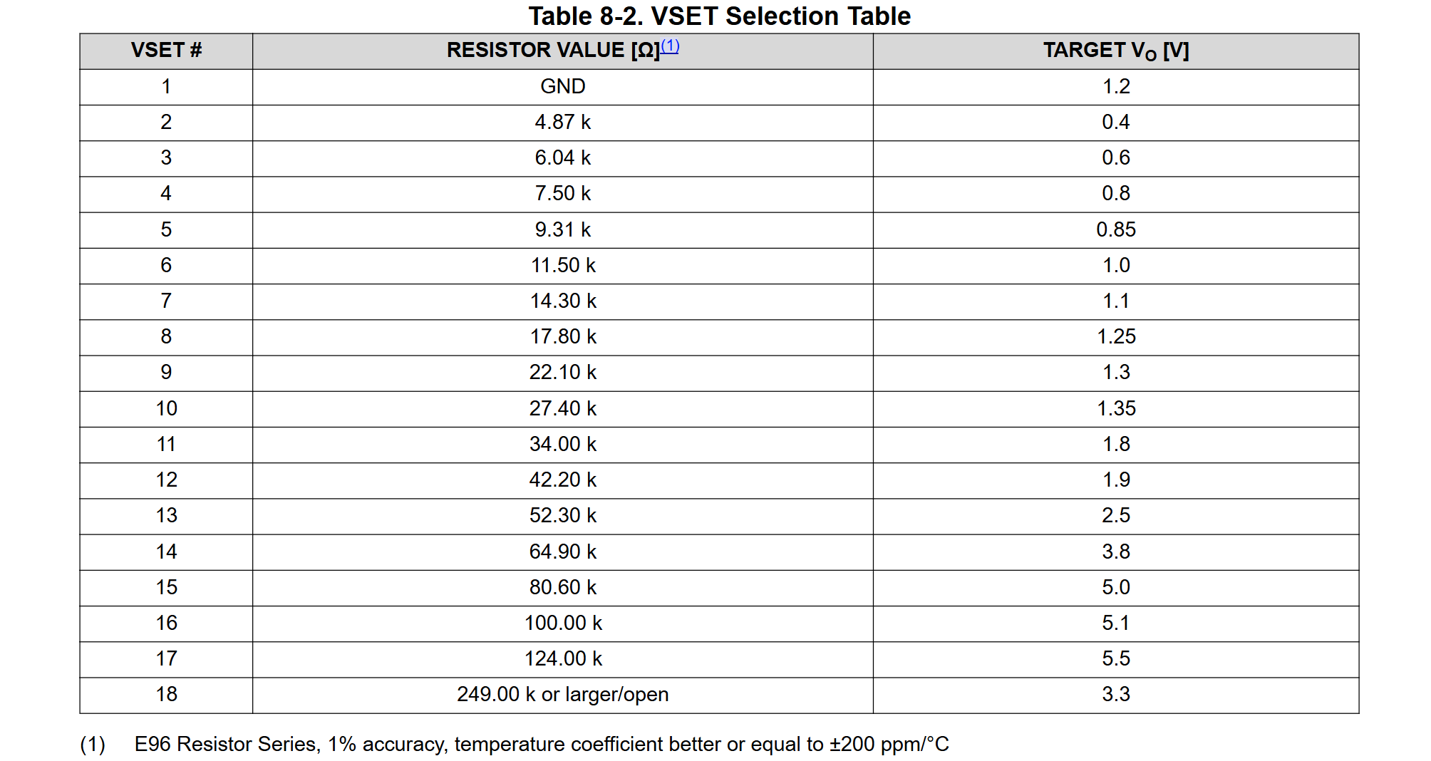
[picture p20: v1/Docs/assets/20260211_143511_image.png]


With E24 resistor (since the votlage is not super critical anyway), we can use either 100k (5.1V) or 82k (5.05V). For simplicity, we just go for 100k as we will probably use it elsewhere.

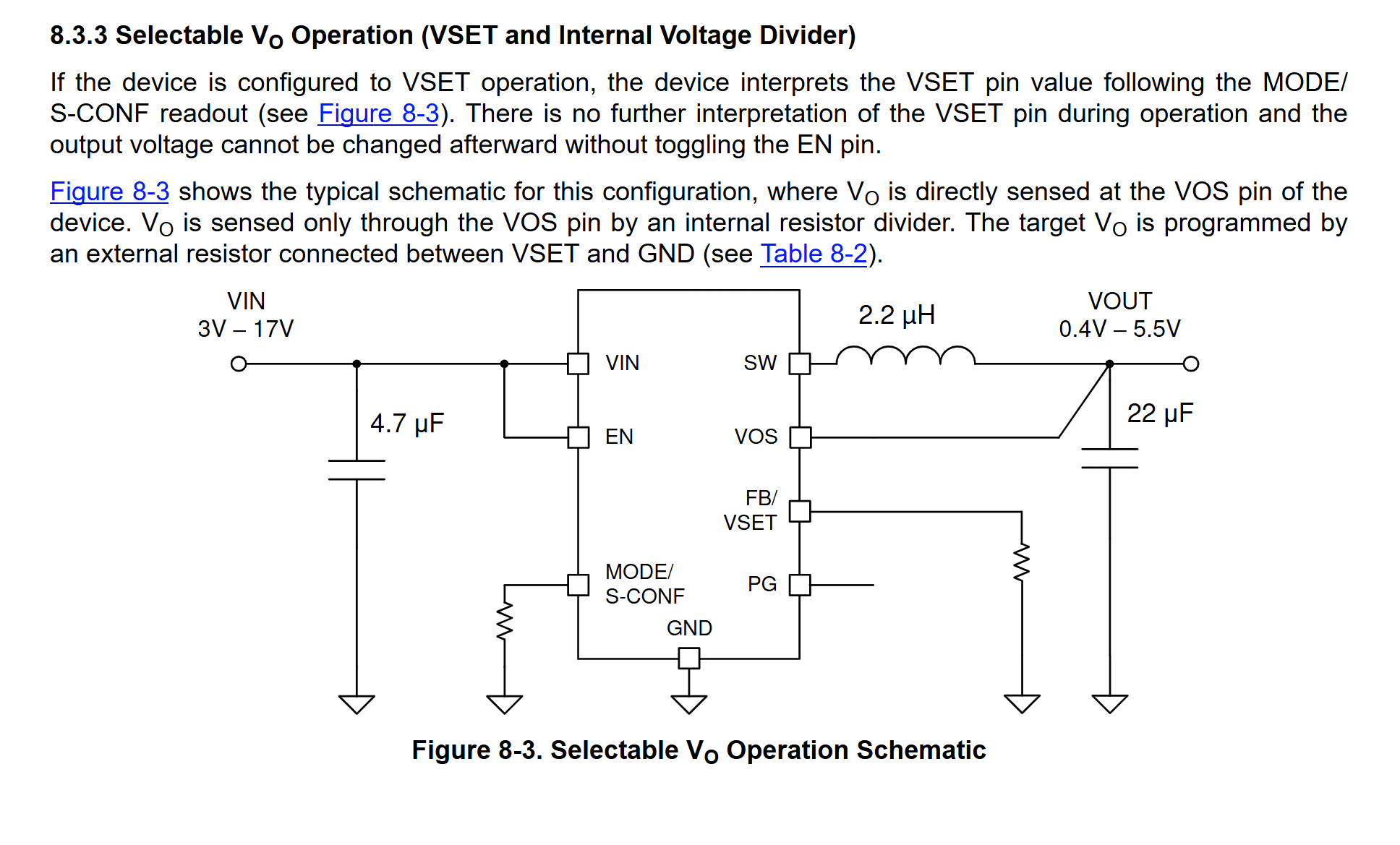
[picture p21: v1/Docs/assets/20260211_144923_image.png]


Mode config:

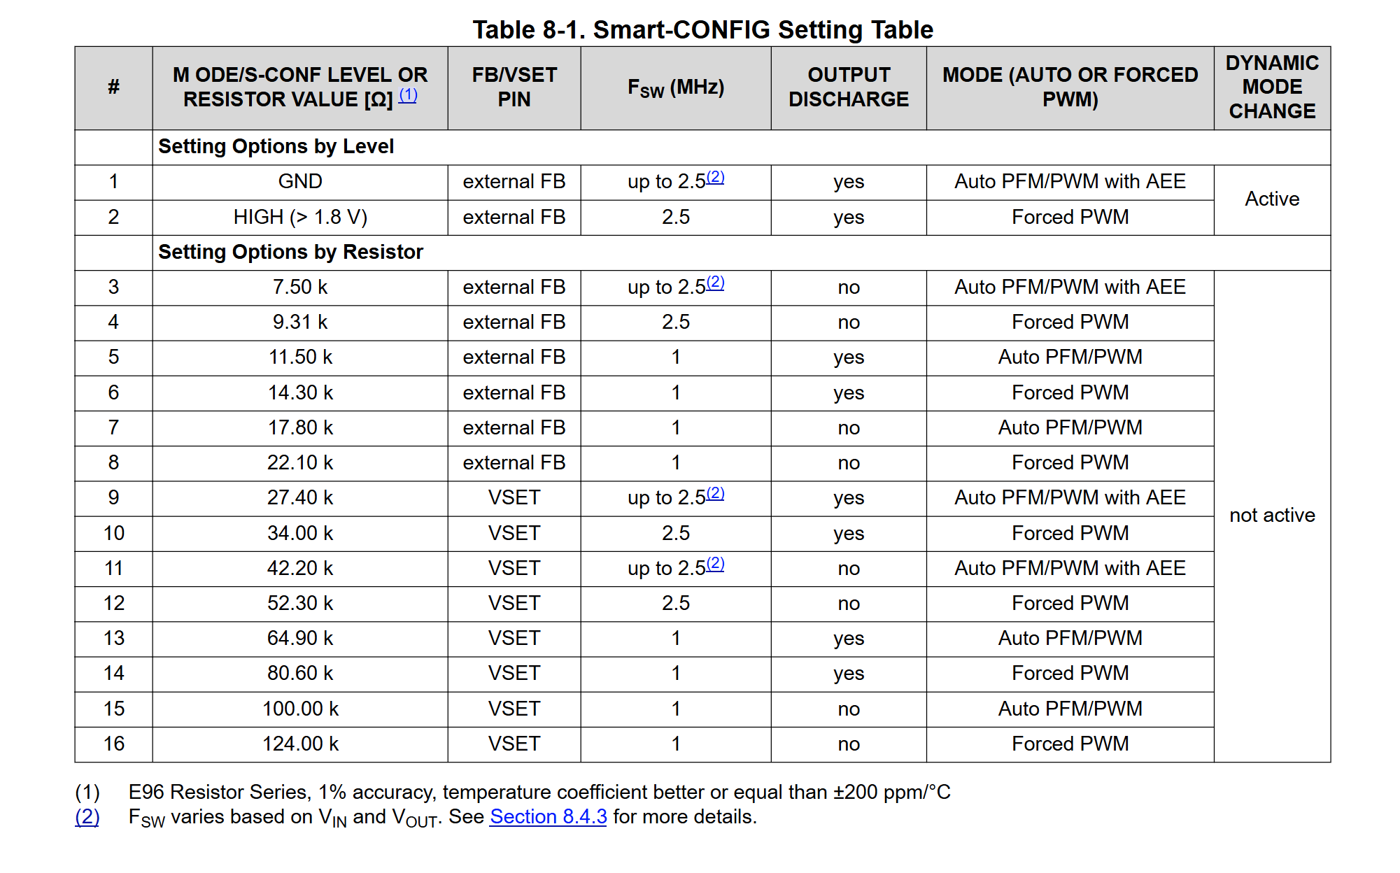
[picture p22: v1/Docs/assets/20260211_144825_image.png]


Recommended inductor:

DFE252012PD-2R2M (Murata, 2.2uH, ~$0.4)

Recommended layout:

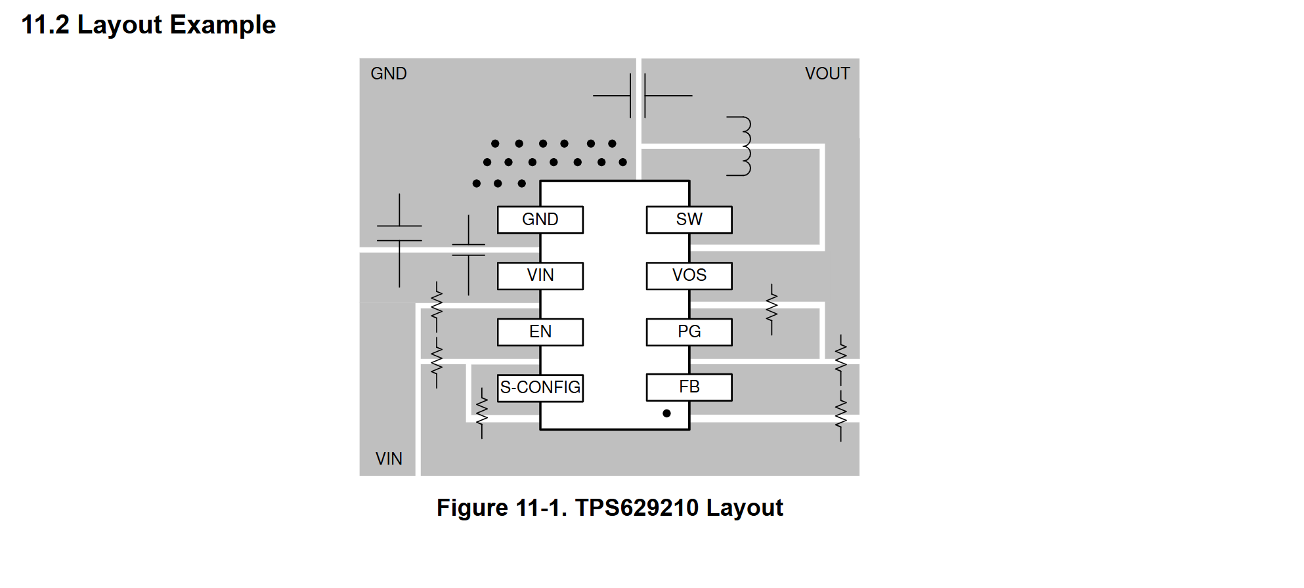
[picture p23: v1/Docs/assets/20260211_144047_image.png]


#### S6.2: Solar battery charger

BQ25186 - takes input from the diode OR. Can handle input voltages up to 18V, but as a linear regulator, this will not work well for efficient battery charging (hence S6.1: buck regulator).

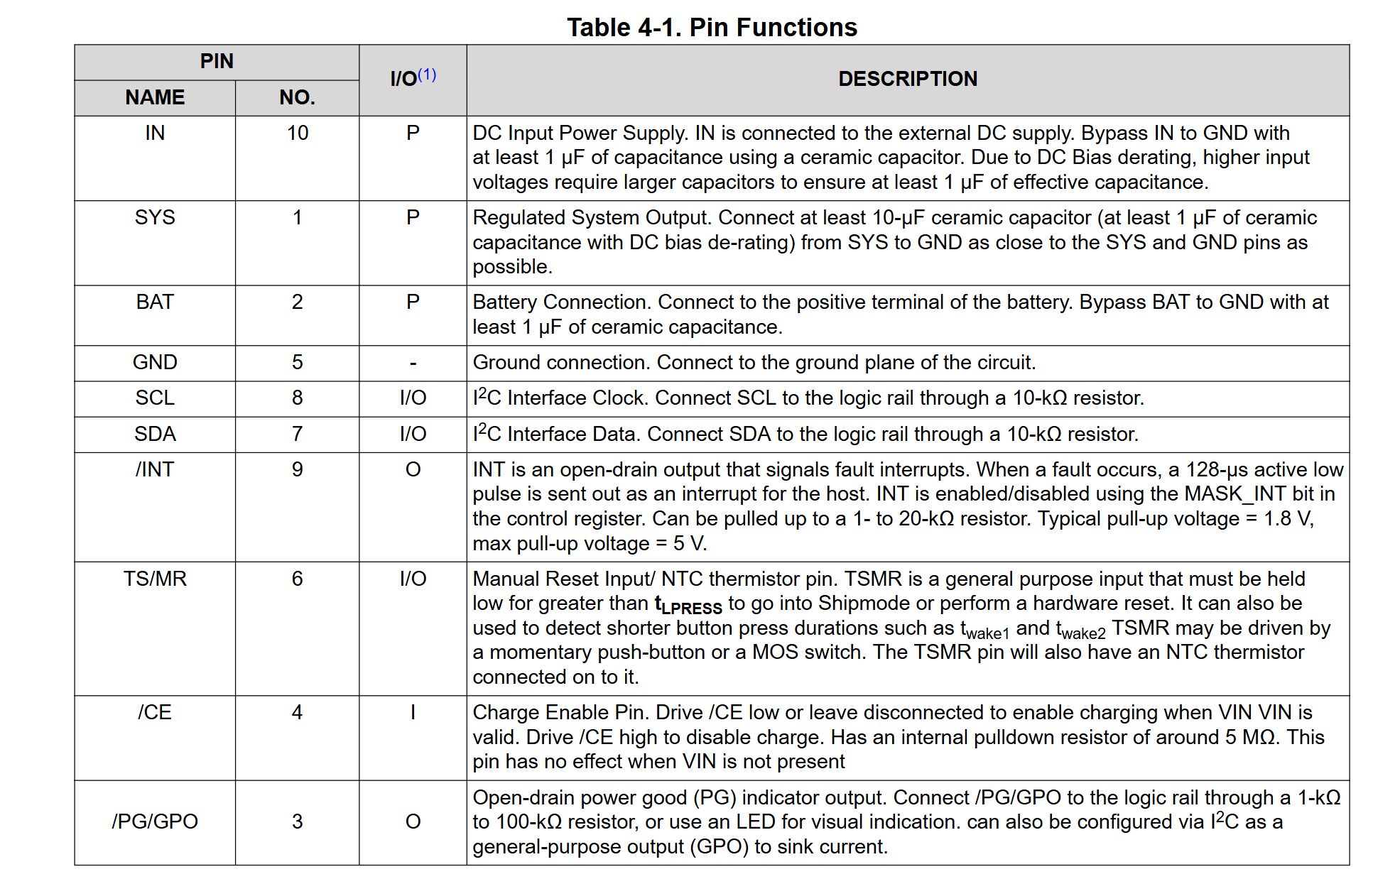
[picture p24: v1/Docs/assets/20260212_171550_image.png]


Diode OR:

- Need a general purpose schottky, comfortable at ~0.5A (max for battery charging AND supplying board).
- Options:
  - SS14 (in larger SMA package)
  - SK14B (in slightly smaller SMB / DO-214AA package)
  - MBR130T1G (in medium SOD-123 package)
  - BAT20J (in small SOD323 package). But 200mA
- Lets go for MBR130T1G: 30V/1A, very widely available.

##### Microphones

###### MIC1

DLFT0 uses SIFT0 with CC0 (common clock0). This allows us to use this microphone by itself (mono mode) either in standard MDF or in the very low power ADF mode (with wakeup).

MIC1 SEL to VCC: Rising edge

PD3: MDF1_SDIO1

PB8: MDF_CC0

###### MIC2+3

PB12 is pin 51 on the LQFP100. But on the schematic it is shown as VDD. Edit the symbol. But then KICAD moved the pins but kept them connected to the *old* stuff. This took some thinking.

*UPDATE: 23/02/2026*: There is something fundamentally incorrect with the pinout of the KiCad model(!) It doesn't have PC4 and PC5! It can't be trusted, so I will have to sort it out manually now 😕

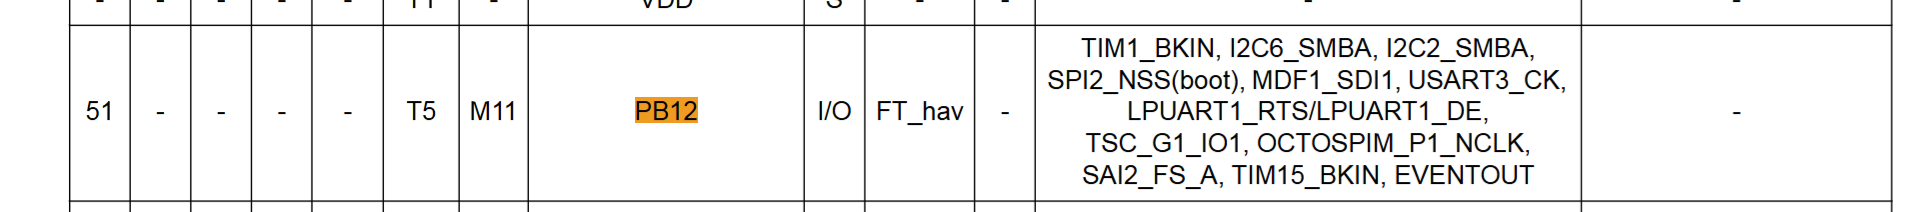
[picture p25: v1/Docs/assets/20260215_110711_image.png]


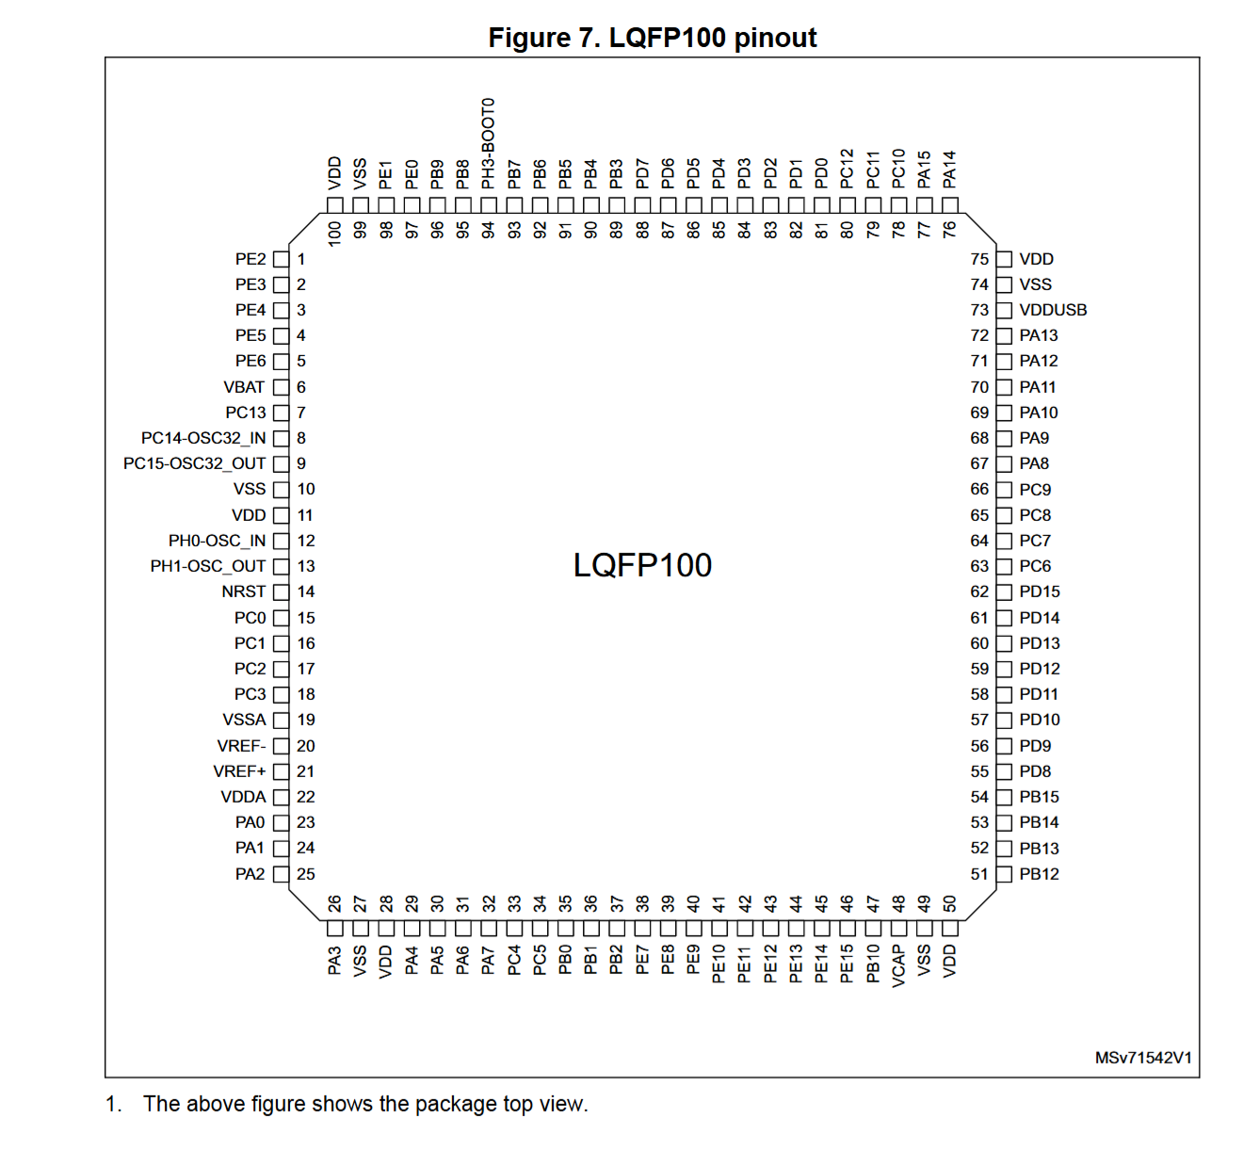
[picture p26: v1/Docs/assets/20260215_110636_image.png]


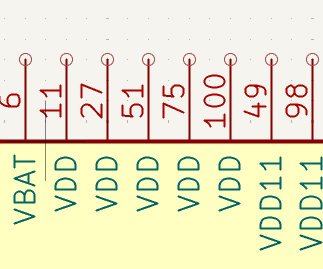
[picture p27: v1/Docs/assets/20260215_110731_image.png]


MIC2: DFLT1, MIC_SD1, CC1, Rising edge PDM

MIC3: DFLT2, MIC_SD1, CC1, Falling edge PDM

MIC4: DFLT3, MIC_SD2, CC1, Rising edge PDM

MIC5: DFLT4, MIC_SD2, CC1, Falling edge PDM

MIC6: DFLT5, MIC_SD3, CC1, Rising edge PDM

#### ACC/MAG

LIS2HH12 in i2c mode. From datasheet `When using the I2C, CS must be tied high (i.e. connected to Vdd_IO).`

#### Extension connector

Tricky to get pure SMD 2x8 header. One option is a molex c-grid **Molex 0015453144** (71395 series) but it has pegs (holes for mechanical support). Looks like we are back to yucky through hole - it seems the only way to get the strength for a larger receptacle. One option that I have found is Amphenol 89898-308ALF which is SMD and relatively well stocked.

Again, we don't have to populate this if we don't want to/need to, but in general, populating now saves soldering later.

FH254V-216-6TBKG79

Choice: 89898-308ALF

On second thoughts, sharing the mikrobus click with a generic extension might get a little tricky. Perhaps a reasonable compromise would be to use the normal 1x8 headers for mikrobus and then have a second extension connector which would also break out programmer pins etc.

These are the pinouts for STM32 SWD (i.e. on the discovery boards):

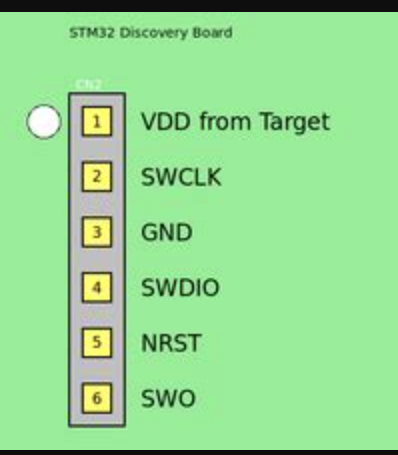
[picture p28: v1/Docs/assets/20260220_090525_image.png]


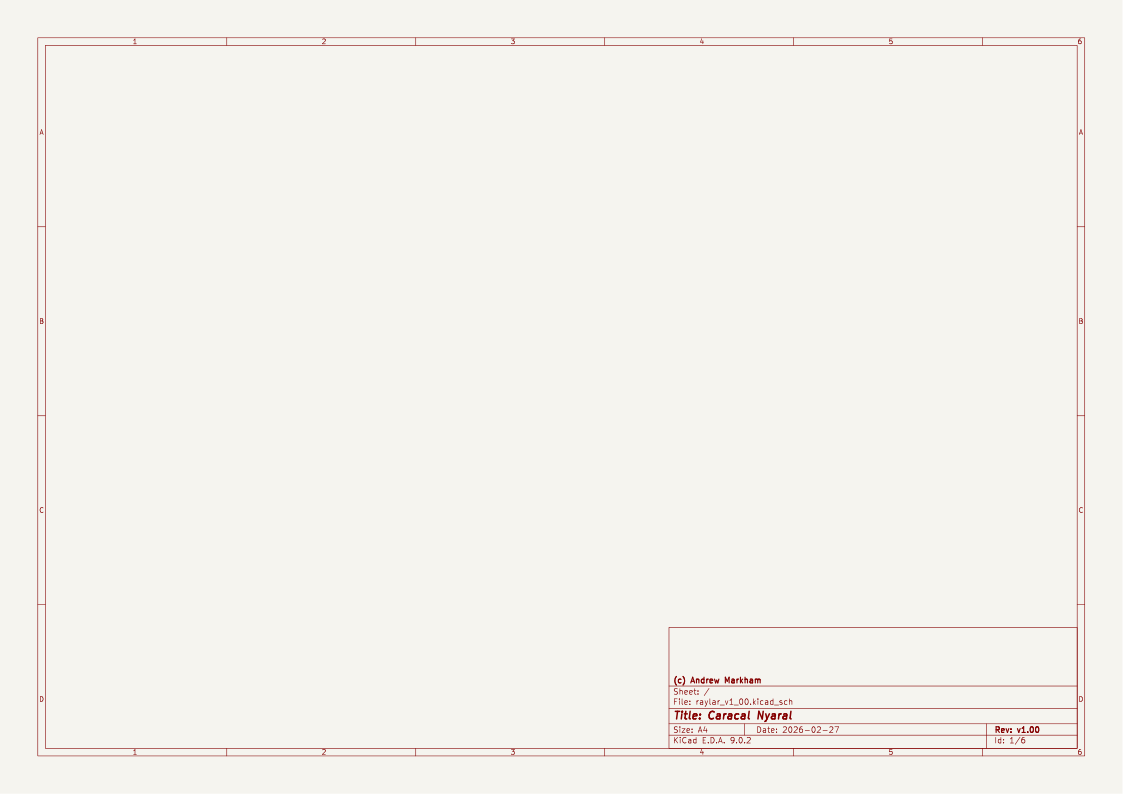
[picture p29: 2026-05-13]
v1/KicadProj/raylar_v1_00/exports/schematics/raylar_v1_00.png

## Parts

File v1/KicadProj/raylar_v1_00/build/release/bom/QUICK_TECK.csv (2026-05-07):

QTY | REFERENCE DESIGNATOR | ITEM DESCRIPTION | SUPPLIER | SUPPLIER PART NO | MANUFACTURER | MANUFACTURER PART NUMBER | LCSC PART NO
18 | C1,C2,C4,C5,C6,C26,C28,C30,C31,C33,C35,C37,C38,C39,C41,C42,C43,C53 | 4.7uF 0402 6.3V capacitor unpolarized | QUICK-TECK | QCC-00294 | SAMSUNG (GENERIC) | CL05A475MP5NRNC | C23733
26 | C3,C7,C8,C9,C10,C11,C16,C18,C19,C25,C27,C29,C32,C34,C36,C40,C44,C45,C46,C47,C48,C49,C50,C51,C52,C54 | 0.1uF 0402 16V capacitor unpolarized | QUICK-TECK | QCC-00426 | MURATA (GENERIC) | GRM155R71H104KE14D | C77020
4 | C12,C13,C14,C15 | 18pF 0402 COG/NPO 50V capacitor unpolarized | QUICK-TECK | QCC-00384 | YAEGO | CC0402JRNPO9BN180 | C106202
6 | C17,C20,C21,C22,C23,C24 | 10uF 0805 25V capacitor unpolarized | QUICK-TECK | QCC-00295 | SAMSUNG | CL21A106KBYQNNE | C2932476
5 | D1,D2,D3,D4,D5 | MBR130T1G SOD123 1A 30V schottky diode | LCSC | C82461 | ON Semiconductor | MBR130T1G | C82461
1 | D8 | 0603 blue LED | QUICK-TECK | QCD-00046 | YONGYUTAI | YLED0603B | C19171394
2 | D9,D11 | 0603 red LED | QUICK-TECK | QCD-00045 | YONGYUTAI | YLED0603R | C19171390
2 | D10,D12 | 0603 green LED | QUICK-TECK | QCD-00048 | YONGYUTAI | YLED0603G | C19273151
2 | J1,J2 | Screw terminal PCB mount 3.5mm pitch 2 terminals | LCSC | C695629 | DORABO | DB301V-3.5-2P-GN-S | C695629
1 | J3 | USB 2.0-only Type-C Receptacle connector | LCSC | C2988369 | G-Switch | GT-USB-7010ASV | C2988369
1 | J4 | JST 2 pin terminal 2mm pitch vertical entry SMD | LCSC | C160352 | JST | B2B-PH-SM4-TB | C160352
1 | J5 | Micro SD socket External Pin | LCSC | C20619272 | CUI | MSD-1-A | C20619272
2 | J6,J10 | 8 pin SMD female header | MOUSER | 640-BG125-8A1144ND | Global Connector Technology | BG125-08-A-1-1-0440-N-D | C6131506
2 | J7,J8 | 4 pin JST 1mm polarized connector for I2C | LCSC | C160404 | JST | SM04B-SRSS-TB | C160404
1 | J9 | AMPHENOL ICC 89898-308ALF Socket strip 2x8p | LCSC | C5417482 | FCI | 89898-308ALF | C5417482
2 | L1,L2 | 2.2 uH, Power Inductor Case:2.5Mm X 2Mm X 1.2Mm 1008 case (2520 metric) | LCSC | C237482 | Murata Electronics | DFE252012PD-2R2M=P2 | C237482
6 | MK1,MK2,MK3,MK4,MK5,MK6 | Digital MEMS Microphone, LGA-5 | MOUSER | 726-IM69D129FV01XTMA | Infineon | IM69D129FV01XTMA1 | C43314439
9 | R1,R2,R13,R15,R31,R32,R33,R34,R38 | Resistor 10k 0402 | QUICK-TECK | QCR-00076 | YAGEO | RC0402JR-0710KL | C60489
2 | R3,R5 | Resistor 180k 0402 | QUICK-TECK | QCR-00102 | YAGEO | RC0402FR-07180KL | C138046
10 | R4,R6,R16,R17,R18,R19,R20,R23,R24,R26 | Resistor 33k 0402 | QUICK-TECK | QCR-00086 | UNI-ROYAL(Uniroyal Elec) | 0402WGF3302TCE | C25779
3 | R7,R8,R35 | Resistor 22R 0402 | QUICK-TECK | QCR-00018 | UNI-ROYAL(Uniroyal Elec) | 0402WGF220JTCE | C25092
3 | R9,R10,R12 | Resistor 5.1k 0402 | LCSC | C25905 | UNI-ROYAL(Uniroyal Elec) | 0402WGF5101TCE | C25905
1 | R11 | Resistor 42.2k E96 0402 | LCSC | C276270 | YAGEO | RC0402FR-0742K2L | C276270
2 | R14,R27 | Resistor 100k 0402 | QUICK-TECK | QCR-00098 | UNI-ROYAL(Uniroyal Elec) | 0402WGF1003TCE | C25741
5 | R25,R29,R30,R36,R37 | Resistor 2.2k 0402 | LCSC | C25879 | UNI-ROYAL(Uniroyal Elec) | 0402WGF2201TCE | C25879
1 | R28 | Resistor 330R 0402 | QUICK-TECK | QCR-00042 | UNI-ROYAL(Uniroyal Elec) | 0402WGF3300TCE | C25104
3 | SW1,SW2,SW3 | Push switch, Single Pole Single Throw (SPST) switch | LCSC | C221676 | C&K | KMR211NGLFS | C221676
1 | U1 | ARM? Cortex?-M33 STM32U5 Microcontroller IC 32-Bit 160MHz 4MB (4M x 8) FLASH 100-LQFP (14x14) | MOUSER | 511-STM32U595VJT6Q | STM | STM32U595VJT6Q | C24591629
1 | U2 | Buck Switching Regulator IC Positive Adjustable 0.4V 1 Output 1A SOT-583 | MOUSER | 595-TPS629210DRLR | Texas Instruments | TPS629210DRLR | C5219301
1 | U3 | BQ25186 1-Cell, 1A I2C Linear Battery Charger with Power Path, Ship Mode,Shutdown Mode, and Battery Tracking VINDPM | MOUSER | 595-BQ25186DLHR | Texas Instruments | BQ25186DLHR | C44639442
1 | U4 | 1A Low IQ Small Size Low Dropout Voltage Regulator, Fixed Output 3.3V, WSON6 | MOUSER | 595-TLV75733PDRVR | Texas Instruments | TLV75733PDRVR | C2868428
1 | U5 | Ebyte E80 LR1121 multi-band LoRa module | LCSC | C42464134 | Chengdu Ebyte Elec Tech | E80-900M2213S | C42464134
1 | U6 | P-Channel 25 V 460mA (Ta) 350mW (Ta) Surface Mount SOT-23-3 | LCSC | C5219301 | ON Semiconductor | FDV304P | C10884
1 | U7 | L86 is an ultra-compact GNSS POT _Patch on Top_ module with an embedded 18.4mm ? 18.4mm ? 4.0mm patch antenna and utilizes the MediaTek new generation GNSS chipset MT3333 that achieves the perfect performance | LCSC | C909689 | Quectel | L86-M33 | C909689
1 | U8 | 3-Axis Accelerometer, 2/4/8g range, I2C/SPI interface | LCSC | C221446 | ST | LIS2HH12 | C221446
1 | U9 | Ultra-low-power, 3-axis digital output magnetometer, LGA-12 | LCSC | C919695 | ST | LIS2MDL | C919695
1 | U10 | Buzzers Transducer, Externally Driven Piezo 3 V 1mA 4kHz 72dB @ 3V, 10cm Surface Mount Solder Pads | MOUSER | 179-CPT-9019A-SMT-TR | CUI Same Sky | CPT-9019A-SMT-TR | C20181991
1 | Y1 | 16 MHz ?20ppm Crystal 12pF 70 Ohms 4-SMD, No Lead | LCSC | C596903 | Abracon | ABM8AIG-16.000MHZ-12-2Z-T3 | C596903
1 | Y2 | 32.768 kHz ?20ppm Crystal 12.5pF 70 kOhms 2-SMD, No Lead | LCSC | C130253 | Abracon | ABS07-32.768KHZ-T | C130253

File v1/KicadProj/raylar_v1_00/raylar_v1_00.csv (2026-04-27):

Refs | Value | Footprint | Qty | DNP
C1 | 4.7uF | PCM_SparkFun-Capacitor:C_0402_1005Metric | 1
C2 | 4.7uF | PCM_SparkFun-Capacitor:C_0402_1005Metric | 1
C3 | 0.1uF | PCM_SparkFun-Capacitor:C_0402_1005Metric | 1
C4 | 4.7uF | PCM_SparkFun-Capacitor:C_0402_1005Metric | 1
C5 | 4.7uF | PCM_SparkFun-Capacitor:C_0402_1005Metric | 1
C6 | 4.7uF | PCM_SparkFun-Capacitor:C_0402_1005Metric | 1
C7 | 0.1uF | PCM_SparkFun-Capacitor:C_0402_1005Metric | 1
C8 | 0.1uF | PCM_SparkFun-Capacitor:C_0402_1005Metric | 1
C9 | 0.1uF | PCM_SparkFun-Capacitor:C_0402_1005Metric | 1
C10 | 0.1uF | PCM_SparkFun-Capacitor:C_0402_1005Metric | 1
C11 | 0.1uF | PCM_SparkFun-Capacitor:C_0402_1005Metric | 1
C12 | 18pF X7R | PCM_SparkFun-Capacitor:C_0402_1005Metric | 1
C13 | 18pF X7R | PCM_SparkFun-Capacitor:C_0402_1005Metric | 1
C14 | 18pF X7R | PCM_SparkFun-Capacitor:C_0402_1005Metric | 1
C15 | 18pF X7R | PCM_SparkFun-Capacitor:C_0402_1005Metric | 1
C16 | 0.1uF | PCM_SparkFun-Capacitor:C_0402_1005Metric | 1
C17 | 10uF | PCM_SparkFun-Capacitor:C_0805_2012Metric | 1
C18 | 0.1uF | PCM_SparkFun-Capacitor:C_0402_1005Metric | 1
C19 | 0.1uF | PCM_SparkFun-Capacitor:C_0402_1005Metric | 1
C20 | 10uF | PCM_SparkFun-Capacitor:C_0805_2012Metric | 1
C21 | 10uF | PCM_SparkFun-Capacitor:C_0805_2012Metric | 1
C22 | 10uF | PCM_SparkFun-Capacitor:C_0805_2012Metric | 1
C23 | 10uF | PCM_SparkFun-Capacitor:C_0805_2012Metric | 1
C24 | 10uF | PCM_SparkFun-Capacitor:C_0805_2012Metric | 1
C25 | 0.1uF | PCM_SparkFun-Capacitor:C_0402_1005Metric | 1
C26 | 4.7uF | PCM_SparkFun-Capacitor:C_0402_1005Metric | 1
C27 | 0.1uF | PCM_SparkFun-Capacitor:C_0402_1005Metric | 1
C28 | 4.7uF | PCM_SparkFun-Capacitor:C_0402_1005Metric | 1
C29 | 0.1uF | PCM_SparkFun-Capacitor:C_0402_1005Metric | 1
C30 | 4.7uF | PCM_SparkFun-Capacitor:C_0402_1005Metric | 1
C31 | 4.7uF | PCM_SparkFun-Capacitor:C_0402_1005Metric | 1
C32 | 0.1uF | PCM_SparkFun-Capacitor:C_0402_1005Metric | 1
C33 | 4.7uF | PCM_SparkFun-Capacitor:C_0402_1005Metric | 1
C34 | 0.1uF | PCM_SparkFun-Capacitor:C_0402_1005Metric | 1
C35 | 4.7uF | PCM_SparkFun-Capacitor:C_0402_1005Metric | 1
C36 | 0.1uF | PCM_SparkFun-Capacitor:C_0402_1005Metric | 1
C37 | 4.7uF | PCM_SparkFun-Capacitor:C_0402_1005Metric | 1
C38 | 4.7uF | PCM_SparkFun-Capacitor:C_0402_1005Metric | 1
C39 | 4.7uF | PCM_SparkFun-Capacitor:C_0402_1005Metric | 1
C40 | 0.1uF | PCM_SparkFun-Capacitor:C_0402_1005Metric | 1
C41 | 4.7uF | PCM_SparkFun-Capacitor:C_0402_1005Metric | 1
C42 | 4.7uF | PCM_SparkFun-Capacitor:C_0402_1005Metric | 1
C43 | 4.7uF | PCM_SparkFun-Capacitor:C_0402_1005Metric | 1
C44 | 0.1uF | PCM_SparkFun-Capacitor:C_0402_1005Metric | 1
C45 | 0.1uF | PCM_SparkFun-Capacitor:C_0402_1005Metric | 1
C46 | 0.1uF | PCM_SparkFun-Capacitor:C_0402_1005Metric | 1
C47 | 0.1uF | PCM_SparkFun-Capacitor:C_0402_1005Metric | 1
C48 | 0.1uF | PCM_SparkFun-Capacitor:C_0402_1005Metric | 1
C49 | 0.1uF | PCM_SparkFun-Capacitor:C_0402_1005Metric | 1
C50 | 0.1uF | PCM_SparkFun-Capacitor:C_0402_1005Metric | 1
C51 | 0.1uF | PCM_SparkFun-Capacitor:C_0402_1005Metric | 1
C52 | 0.1uF | PCM_SparkFun-Capacitor:C_0402_1005Metric | 1
C53 | 4.7uF | PCM_SparkFun-Capacitor:C_0402_1005Metric | 1
C54 | 0.1uF | PCM_SparkFun-Capacitor:C_0402_1005Metric | 1
D1 | MBR130T1G | MBR0530T1G:DIO_MBR0530T1G | 1
D2 | MBR130T1G | MBR0530T1G:DIO_MBR0530T1G | 1
D3 | MBR130T1G | MBR0530T1G:DIO_MBR0530T1G | 1
D4 | MBR130T1G | MBR0530T1G:DIO_MBR0530T1G | 1
D5 | MBR130T1G | MBR0530T1G:DIO_MBR0530T1G | 1
D8 | Blue | PCM_SparkFun-LED:LED_0603_1608Metric_Blue | 1
D9 | Red | PCM_SparkFun-LED:LED_0603_1608Metric_Red | 1
D10 | Green | PCM_SparkFun-LED:LED_0603_1608Metric_Green | 1
D11 | Red | PCM_SparkFun-LED:LED_0603_1608Metric_Red | 1
D12 | Green | PCM_SparkFun-LED:LED_0603_1608Metric_Green | 1
J1 | 3.5mm | PCM_SparkFun-Connector:ScrewTerminal_1x02_P3.5mm_Horizontal_Black | 1
J2 | 3.5mm | PCM_SparkFun-Connector:ScrewTerminal_1x02_P3.5mm_Horizontal_Black | 1
J3 | USB_C_Receptacle | PCM_SparkFun-Connector:USB-C_16 | 1
J4 | B2B-PH-SM4-TB | B2B-PH-SM4-TB:JST_B2B-PH-SM4-TB | 1
J5 | microSD | PCM_SparkFun-Connector:microSD_External_Pin | 1
J6 | Conn_01x08 | PCM_SparkFun-Connector:1x08_P2.54mm_Socket_Vertical_SMD_Pin1RightDown | 1
J7 | Qwiic_RA | PCM_SparkFun-Connector:JST_1x04_P1.0mm_Horizontal_SMD | 1
J8 | Qwiic_RA | PCM_SparkFun-Connector:JST_1x04_P1.0mm_Horizontal_SMD | 1
J9 | 89898-308ALF | 89898-308ALF:AMPHENOL_89898-308ALF | 1
J10 | Conn_01x08 | PCM_SparkFun-Connector:1x08_P2.54mm_Socket_Vertical_SMD_Pin1RightDown | 1
JP1 | ~ | PCM_SparkFun-Jumper:Jumper_2_NC_Trace | 1
JP2 | ~ | PCM_SparkFun-Jumper:Jumper_2_NO | 1
JP3 | ~ | PCM_SparkFun-Jumper:Jumper_2_NC_Trace | 1
JP4 | ~ | PCM_SparkFun-Jumper:Jumper_2_NC_Trace | 1
JP5 | ~ | PCM_SparkFun-Jumper:Jumper_2_NC_Trace | 1
JP6 | ~ | PCM_SparkFun-Jumper:Jumper_2_NC_Trace | 1
JP7 | ~ | PCM_SparkFun-Jumper:Jumper_2_NC_Trace | 1
JP8 | ~ | PCM_SparkFun-Jumper:Jumper_2_NC_Trace | 1
L1 | DFE252012PD-2R2M=P2 | DFE252012PD-2R2M_P2:INDC2520X120N | 1
L2 | DFE252012PD-2R2M=P2 | DFE252012PD-2R2M_P2:INDC2520X120N | 1
MK1 | IM69D129FV01 | Sensor_Audio:Knowles_LGA-5_3.5x2.65mm | 1
MK2 | IM69D129FV01 | Sensor_Audio:Knowles_LGA-5_3.5x2.65mm | 1
MK3 | IM69D129FV01 | Sensor_Audio:Knowles_LGA-5_3.5x2.65mm | 1
MK4 | IM69D129FV01 | Sensor_Audio:Knowles_LGA-5_3.5x2.65mm | 1
MK5 | IM69D129FV01 | Sensor_Audio:Knowles_LGA-5_3.5x2.65mm | 1
MK6 | IM69D129FV01 | Sensor_Audio:Knowles_LGA-5_3.5x2.65mm | 1
R1 | 10k | PCM_SparkFun-Resistor:R_0402_1005Metric | 1
R2 | 10k | PCM_SparkFun-Resistor:R_0402_1005Metric | 1
R3 | 180k | PCM_SparkFun-Resistor:R_0402_1005Metric | 1
R4 | 33k | PCM_SparkFun-Resistor:R_0402_1005Metric | 1
R5 | 180k | PCM_SparkFun-Resistor:R_0402_1005Metric | 1
R6 | 33k | PCM_SparkFun-Resistor:R_0402_1005Metric | 1
R7 | 22 | PCM_SparkFun-Resistor:R_0402_1005Metric | 1
R8 | 22 | PCM_SparkFun-Resistor:R_0402_1005Metric | 1
R9 | 5.1k | PCM_SparkFun-Resistor:R_0402_1005Metric | 1
R10 | 5.1k | PCM_SparkFun-Resistor:R_0402_1005Metric | 1
R11 | 42.2k E96 | PCM_SparkFun-Resistor:R_0402_1005Metric | 1
R12 | 5.1k | PCM_SparkFun-Resistor:R_0402_1005Metric | 1
R13 | 10k | PCM_SparkFun-Resistor:R_0402_1005Metric | 1
R14 | 100k | PCM_SparkFun-Resistor:R_0402_1005Metric | 1
R15 | 10k | PCM_SparkFun-Resistor:R_0402_1005Metric | 1
R16 | 33k | PCM_SparkFun-Resistor:R_0402_1005Metric | 1
R17 | 33k | PCM_SparkFun-Resistor:R_0402_1005Metric | 1
R18 | 33k | PCM_SparkFun-Resistor:R_0402_1005Metric | 1
R19 | 33k | PCM_SparkFun-Resistor:R_0402_1005Metric | 1
R20 | 33k | PCM_SparkFun-Resistor:R_0402_1005Metric | 1
R23 | 33k | PCM_SparkFun-Resistor:R_0402_1005Metric | 1
R24 | 33k | PCM_SparkFun-Resistor:R_0402_1005Metric | 1
R25 | 2.2k | PCM_SparkFun-Resistor:R_0402_1005Metric | 1
R26 | 33k | PCM_SparkFun-Resistor:R_0402_1005Metric | 1
R27 | 100k | PCM_SparkFun-Resistor:R_0402_1005Metric | 1
R28 | 330 | PCM_SparkFun-Resistor:R_0402_1005Metric | 1
R29 | 2.2k | PCM_SparkFun-Resistor:R_0402_1005Metric | 1
R30 | 2.2k | PCM_SparkFun-Resistor:R_0402_1005Metric | 1
R31 | 10k | PCM_SparkFun-Resistor:R_0402_1005Metric | 1
R32 | 10k | PCM_SparkFun-Resistor:R_0402_1005Metric | 1
R33 | 10k | PCM_SparkFun-Resistor:R_0402_1005Metric | 1
R34 | 10k | PCM_SparkFun-Resistor:R_0402_1005Metric | 1
R35 | 22 | PCM_SparkFun-Resistor:R_0402_1005Metric | 1
R36 | 2.2k | PCM_SparkFun-Resistor:R_0402_1005Metric | 1
R37 | 2.2k | PCM_SparkFun-Resistor:R_0402_1005Metric | 1
R38 | 10k | PCM_SparkFun-Resistor:R_0402_1005Metric | 1
SW1 | SMD_4.6x2.8mm | PCM_SparkFun-Switch:Push_SMD_4.6x2.8mm_h1.9mm | 1
SW2 | SMD_4.6x2.8mm | PCM_SparkFun-Switch:Push_SMD_4.6x2.8mm_h1.9mm | 1
SW3 | SMD_4.6x2.8mm | PCM_SparkFun-Switch:Push_SMD_4.6x2.8mm_h1.9mm | 1
TP1 | 0.5mm | PCM_SparkFun-Connector:TestPoint-0.5mm | 1
TP2 | 0.5mm | PCM_SparkFun-Connector:TestPoint-0.5mm | 1
TP3 | 0.5mm | PCM_SparkFun-Connector:TestPoint-0.5mm | 1
TP4 | 0.5mm | PCM_SparkFun-Connector:TestPoint-0.5mm | 1
TP5 | 0.5mm | PCM_SparkFun-Connector:TestPoint-0.5mm | 1
TP6 | 0.5mm | PCM_SparkFun-Connector:TestPoint-0.5mm | 1
TP7 | 0.5mm | PCM_SparkFun-Connector:TestPoint-0.5mm | 1
TP8 | 0.5mm | PCM_SparkFun-Connector:TestPoint-0.5mm | 1
U1 | STM32U5G7VJTxQ | Package_QFP:LQFP-100_14x14mm_P0.5mm | 1
U2 | TPS629210DRLR | TPS629210:SOT50P160X60-8N | 1
U3 | BQ25186 | BQ25186:IC_BQ25185DLHR | 1
U4 | TLV75733PDRV | PCM_SparkFun-Semiconductor-Standard:WDFN-6_2x2mm | 1
U5 | E80-900M2213S | ebyte:E80-x00M2213S | 1
U6 | FDV304P | FDV304P:SOT23-3 | 1
U7 | L86-M33 | L86-M33:XCVR_L86-M33 | 1
U8 | LIS2HH12 | Package_LGA:LGA-12_2x2mm_P0.5mm | 1
U9 | LIS2MDL | Package_LGA:LGA-12_2x2mm_P0.5mm | 1
U10 | CPT-9019A-SMT-TR | CUI_CPT_9019S:XDCR_CPT-9019A-SMT-TR | 1
Y1 | ABM8AIG-16.000MHZ-12-2Z-T3 | PCM_SparkFun-Clock:Crystal_SMD_3.2x2.5mm | 1
Y2 | 32.768kHz ABS07-32.768KHZ-T | PCM_SparkFun-Clock:Crystal_SMD_3.2x1.5mm | 1

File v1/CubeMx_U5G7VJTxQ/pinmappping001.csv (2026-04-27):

Position | Name | Type | Signal | f | AF0 | AF1 | AF2 | AF3 | AF4 | AF5 | AF6 | AF7 | AF8 | AF9 | AF10 | AF11 | AF12 | AF13 | AF14 | AF15
1 | PE2 | Output | GPIO_Output | MBUS_RST | DEBUG_TRACECLK |  | TIM3_ETR | SAI1_CK1 |  |  |  | USART6_CK | LTDC_R0 | TSC_G7_IO1 |  |  | FMC_A23 | SAI1_MCLK_A |  | EVENTOUT
2 | PE3 | Output | GPIO_Output | MBUS_CS | DEBUG_TRACED0 |  | TIM3_CH1 | OCTOSPIM_P1_DQS |  |  |  | USART6_CTS | LTDC_R1 | TSC_G7_IO2 |  |  | FMC_A19 | SAI1_SD_B |  | EVENTOUT
3 | PE4 | I/O | MDF1_SDI3 | MIC_SD3 | DEBUG_TRACED1 |  | TIM3_CH2 | SAI1_D2 |  |  | MDF1_SDI3 | USART6_DE/USART6_RTS | LTDC_B0 | TSC_G7_IO3 | DCMI_D4/PSSI_D4 |  | FMC_A20 | SAI1_FS_A |  | EVENTOUT
4 | PE5 | I/O | GPIO_EXTI5 | MBUS_INT | DEBUG_TRACED2 |  | TIM3_CH3 | SAI1_CK2 |  |  | MDF1_CKI3 |  | LTDC_G0 | TSC_G7_IO4 | DCMI_D6/PSSI_D6 |  | FMC_A21 | SAI1_SCK_A |  | EVENTOUT
5 | PE6 | Input | GPIO_Input | SW_USER | DEBUG_TRACED3 |  | TIM3_CH4 | SAI1_D1 |  |  |  |  | LTDC_G1 |  | DCMI_D7/PSSI_D7 |  | FMC_A22 | SAI1_SD_A |  | EVENTOUT
6 | VBAT | Power
7 | PC13 | Output | GPIO_Output | SYS_MAIN_GREEN |  |  |  |  |  |  |  |  |  |  |  |  |  |  |  | EVENTOUT
8 | PC14-OSC32_IN (PC14) | I/O | RCC_OSC32_IN | OSC_32K_IN |  |  |  |  |  |  |  |  |  |  |  |  |  |  |  | EVENTOUT
9 | PC15-OSC32_OUT (PC15) | I/O | RCC_OSC32_OUT | OSC_32K_OUT |  |  |  |  |  |  |  |  |  |  |  |  |  |  |  | EVENTOUT
10 | VSS | Power
11 | VDD | Power
12 | PH0-OSC_IN (PH0) | I/O | RCC_OSC_IN | HSE_OSC_IN |  |  |  |  |  |  |  |  |  |  |  |  |  |  |  | EVENTOUT
13 | PH1-OSC_OUT (PH1) | I/O | RCC_OSC_OUT | HE_OSC_OUT |  |  |  |  |  |  |  |  |  |  |  |  |  |  |  | EVENTOUT
14 | NRST | Reset
15 | PC0 | I/O | I2C3_SCL | MBUS_SCL |  | LPTIM1_IN1 | GFXTIM_FCKCAL | OCTOSPIM_P1_IO7 | I2C3_SCL | SPI2_RDY | MDF1_SDI4 | USART6_CTS | LPUART1_RX |  |  | GFXTIM_LCKCAL | SDMMC1_D5 | SAI2_FS_A | LPTIM2_IN1 | EVENTOUT
16 | PC1 | I/O | I2C3_SDA | MBUS_SDA | DEBUG_TRACED0 | LPTIM1_CH1 |  | SPI2_MOSI | I2C3_SDA |  | MDF1_CKI4 | USART6_CK | LPUART1_TX |  | OCTOSPIM_P1_IO4 |  | SDMMC2_CK | SAI1_SD_A |  | EVENTOUT
17 | PC2 | I/O | MDF1_CCK1 | MIC_CCLK1 |  | LPTIM1_IN2 |  |  |  | SPI2_MISO | MDF1_CCK1 | USART6_RX |  |  | OCTOSPIM_P1_IO5 |  |  |  |  | EVENTOUT
18 | PC3 | I/O | SPI2_MOSI | MBUS_MOSI |  | LPTIM1_ETR | LPTIM3_CH1 | SAI1_D1 |  | SPI2_MOSI |  | USART6_TX |  |  | OCTOSPIM_P1_IO6 |  |  | SAI1_SD_A | LPTIM2_ETR | EVENTOUT
19 | VSSA | Power
20 | VREF+ | MonoIO | VREFBUF_OUT
21 | VDDA | Power
22 | PA0 | I/O |  |  |  | TIM2_CH1 | TIM5_CH1 | TIM8_ETR |  |  | SPI3_RDY | USART2_CTS | UART4_TX |  | OCTOSPIM_P2_NCS |  | SDMMC2_CMD | AUDIOCLK | TIM2_ETR | EVENTOUT
23 | PA1 | I/O | ADC1_IN6 | MBUS_AN | LPTIM1_CH2 | TIM2_CH2 | TIM5_CH2 |  | I2C1_SMBA | SPI1_SCK |  | USART2_DE/USART2_RTS | UART4_RX |  | OCTOSPIM_P1_DQS |  |  |  | TIM15_CH1N | EVENTOUT
24 | PA2 | I/O | ADC1_IN7 | V_ADC_SOLAR |  | TIM2_CH3 | TIM5_CH3 |  |  | SPI1_RDY |  | USART2_TX | LPUART1_TX |  | OCTOSPIM_P1_NCS | UCPD1_FRSTX1 |  |  | TIM15_CH1 | EVENTOUT
25 | PA3 | I/O | ADC1_IN8 | V_ADC_DC |  | TIM2_CH4 | TIM5_CH4 | SAI1_CK1 |  |  |  | USART2_RX | LPUART1_RX |  | OCTOSPIM_P1_CLK |  |  | SAI1_MCLK_A | TIM15_CH2 | EVENTOUT
26 | VSS | Power
27 | VDD | Power
28 | PA4 | I/O | ADC1_IN9 | V_ADC_BATT |  |  |  | OCTOSPIM_P1_NCS |  | SPI1_NSS | SPI3_NSS | USART2_CK |  |  | DCMI_HSYNC/PSSI_DE |  |  | SAI1_FS_B | LPTIM2_CH1 | EVENTOUT
29 | PA5 | I/O | TIM8_CH1N DAC1_OUT2 | BUZ | PWR_CSLEEP | TIM2_CH1 | TIM2_ETR | TIM8_CH1N | PSSI_D14 | SPI1_SCK |  | USART3_RX |  |  |  |  |  |  | LPTIM2_ETR | EVENTOUT
30 | PA6 | I/O | OPAMP2_VINP | EXT_OPA_VINP | PWR_CDSTOP | TIM1_BKIN | TIM3_CH1 | TIM8_BKIN | DCMI_PIXCLK/PSSI_PDCK | SPI1_MISO |  | USART3_CTS | LPUART1_CTS |  | OCTOSPIM_P1_IO3 |  |  |  | TIM16_CH1 | EVENTOUT
31 | PA7 | I/O | OPAMP2_VINM | EXT_OPA_VINM | PWR_SRDSTOP | TIM1_CH1N | TIM3_CH2 | TIM8_CH1N | I2C3_SCL | SPI1_MOSI |  | USART3_TX |  |  | OCTOSPIM_P1_IO2 |  |  | LPTIM2_CH2 | TIM17_CH1 | EVENTOUT
32 | PB0 | I/O | OPAMP2_VOUT | EXT_OPA_VOUT |  | TIM1_CH2N | TIM3_CH3 | TIM8_CH2N | LPTIM3_CH1 | SPI1_NSS |  | USART3_CK |  |  | OCTOSPIM_P1_IO1 |  | COMP1_OUT | AUDIOCLK |  | EVENTOUT
33 | PB1 | I/O | ADC1_IN16 | EXT_AN_IN |  | TIM1_CH3N | TIM3_CH4 | TIM8_CH3N | LPTIM3_CH2 |  | MDF1_SDI0 | USART3_DE/USART3_RTS | LPUART1_DE/LPUART1_RTS |  | OCTOSPIM_P1_IO0 |  |  |  | LPTIM2_IN1 | EVENTOUT
34 | PB2 | I/O |  |  |  | LPTIM1_CH1 |  | TIM8_CH4N | I2C3_SMBA | SPI1_RDY | MDF1_CKI0 |  | LTDC_B1 |  | OCTOSPIM_P1_DQS | UCPD1_FRSTX1 |  |  |  | EVENTOUT
35 | PE7 | I/O | MDF1_SDI2 | MIC_SD2 |  | TIM1_ETR |  |  |  |  | MDF1_SDI2 |  | LTDC_B6 |  |  |  | FMC_D4/FMC_DA4 | SAI1_SD_B |  | EVENTOUT
36 | PE8 | Output | GPIO_Output | RF_CS |  | TIM1_CH1N |  |  |  |  | MDF1_CKI2 |  | LTDC_B7 |  |  |  | FMC_D5/FMC_DA5 | SAI1_SCK_B |  | EVENTOUT
37 | PE9 | I/O | MDF1_CCK0 | MIC_CCLK0 |  | TIM1_CH1 |  | ADF1_CCK0 |  |  | MDF1_CCK0 |  | LTDC_G2 |  | OCTOSPIM_P1_NCLK |  | FMC_D6/FMC_DA6 | SAI1_FS_B |  | EVENTOUT
38 | PE10 | Input | GPIO_Input | RF_BUSY |  | TIM1_CH2N |  | ADF1_SDI0 |  |  | MDF1_SDI4 |  | LTDC_G3 | TSC_G5_IO1 | OCTOSPIM_P1_CLK |  | FMC_D7/FMC_DA7 | SAI1_MCLK_B |  | EVENTOUT
39 | PE11 | Output | GPIO_Output | RF_NRST |  | TIM1_CH2 |  |  |  | SPI1_RDY | MDF1_CKI4 |  | LTDC_G4 | TSC_G5_IO2 | OCTOSPIM_P1_NCS |  | FMC_D8/FMC_DA8 |  |  | EVENTOUT
40 | PE12 | I/O | GPIO_EXTI12 | RF_IRQ |  | TIM1_CH3N |  |  |  | SPI1_NSS | MDF1_SDI5 |  | LTDC_G5 | TSC_G5_IO3 | OCTOSPIM_P1_IO0 |  | FMC_D9/FMC_DA9 |  |  | EVENTOUT
41 | PE13 | I/O | SPI1_SCK | RF_SCK |  | TIM1_CH3 |  |  |  | SPI1_SCK | MDF1_CKI5 |  | LTDC_G6 | TSC_G5_IO4 | OCTOSPIM_P1_IO1 |  | FMC_D10/FMC_DA10 |  |  | EVENTOUT
42 | PE14 | I/O | SPI1_MISO | RF_MISO |  | TIM1_CH4 | TIM1_BKIN2 |  |  | SPI1_MISO |  |  | LTDC_G7 |  | OCTOSPIM_P1_IO2 |  | FMC_D11/FMC_DA11 | GFXTIM_LCKCAL |  | EVENTOUT
43 | PE15 | I/O | SPI1_MOSI | RF_MOSI |  | TIM1_BKIN | GFXTIM_LCKCAL | TIM1_CH4N |  | SPI1_MOSI |  |  | LTDC_R2 |  | OCTOSPIM_P1_IO3 |  | FMC_D12/FMC_DA12 | GFXTIM_FCKCAL |  | EVENTOUT
44 | PB10 | I/O | I2C4_SCL | QWIIC_SCL |  | TIM2_CH3 | LPTIM3_CH1 | I2C4_SCL | I2C2_SCL | SPI2_SCK |  | USART3_TX | LPUART1_RX | TSC_SYNC | OCTOSPIM_P1_CLK |  | COMP1_OUT | SAI1_SCK_A |  | EVENTOUT
45 | PB11 | I/O | USART3_RX | GPS_TX_STM_RX |  | TIM2_CH4 |  | I2C4_SDA | I2C2_SDA | SPI2_RDY |  | USART3_RX | LPUART1_TX |  | OCTOSPIM_P1_NCS |  | COMP2_OUT |  |  | EVENTOUT
46 | VLXSMPS | Power
47 | VDDSMPS | Power
48 | VSSSMPS | Power
49 | VDD11 | Power
50 | VSS | Power
51 | VDD | Power
52 | PB13 | I/O | SPI2_SCK | MBUS_SCK |  | TIM1_CH1N | LPTIM3_IN1 |  | I2C2_SCL | SPI2_SCK | MDF1_CKI1 | USART3_CTS | LPUART1_CTS | TSC_G1_IO2 |  |  |  | SAI2_SCK_A | TIM15_CH1N | EVENTOUT
53 | PB14 | I/O | SPI2_MISO | MBUS_MISO |  | TIM1_CH2N | LPTIM3_ETR | TIM8_CH2N | I2C2_SDA | SPI2_MISO | MDF1_SDI2 | USART3_DE/USART3_RTS |  | TSC_G1_IO3 |  |  | SDMMC2_D0 | SAI2_MCLK_A | TIM15_CH1 | EVENTOUT
54 | PB15 | I/O |  |  | RTC_REFIN | TIM1_CH3N | LPTIM2_IN2 | TIM8_CH3N |  | SPI2_MOSI | MDF1_CKI2 |  |  |  | GFXTIM_TE | FMC_NBL1 | SDMMC2_D1 | SAI2_SD_A | TIM15_CH2 | EVENTOUT
55 | PD8 | I/O | USART3_TX | GPS_RX_STM_TX |  |  |  |  |  |  |  | USART3_TX | LTDC_R3 |  | DCMI_HSYNC/PSSI_DE |  | FMC_D13/FMC_DA13 |  |  | EVENTOUT
56 | PD9 | I/O | GPIO_EXTI9 | GPS_PPS |  |  | LPTIM2_IN2 |  |  |  |  | USART3_RX | LTDC_R4 |  | DCMI_PIXCLK/PSSI_PDCK |  | FMC_D14/FMC_DA14 | SAI2_MCLK_A | LPTIM3_IN1 | EVENTOUT
57 | PD10 | Output | GPIO_Output | GPS_EN |  |  | LPTIM2_CH2 |  | I2C5_SMBA |  |  | USART3_CK | LTDC_R5 | TSC_G6_IO1 |  |  | FMC_D15/FMC_DA15 | SAI2_SCK_A | LPTIM3_ETR | EVENTOUT
58 | PD11 | Output | GPIO_Output | GPS_RST |  |  |  |  | I2C4_SMBA |  |  | USART3_CTS | LTDC_R6 | TSC_G6_IO2 |  |  | FMC_A16/FMC_CLE | SAI2_SD_A | LPTIM2_ETR | EVENTOUT
59 | PD12 | I/O | TIM4_CH1 | MBUS_PWM |  |  | TIM4_CH1 |  | I2C4_SCL |  |  | USART3_DE/USART3_RTS | LTDC_R7 | TSC_G6_IO3 |  |  | FMC_A17/FMC_ALE | SAI2_FS_A | LPTIM2_IN1 | EVENTOUT
60 | PD13 | I/O | I2C4_SDA | QWIIC_SDA |  |  | TIM4_CH2 |  | I2C4_SDA | GFXTIM_TE |  | USART6_CTS | LTDC_VSYNC | TSC_G6_IO4 |  |  | FMC_A18 | LPTIM4_IN1 | LPTIM2_CH1 | EVENTOUT
61 | PD14 | Output | GPIO_Output | SYS_GPS_GREEN |  |  | TIM4_CH3 |  |  |  |  | USART6_CK | LTDC_B2 |  |  |  | FMC_D0/FMC_DA0 |  | LPTIM3_CH1 | EVENTOUT
62 | PD15 | Output | GPIO_Output | SYS_GPS_RED |  |  | TIM4_CH4 |  |  |  |  | USART6_DE/USART6_RTS | LTDC_B3 |  |  |  | FMC_D1/FMC_DA1 |  | LPTIM3_CH2 | EVENTOUT
63 | PC6 | Output | GPIO_Output | SYS_RF_GREEN | PWR_CSLEEP |  | TIM3_CH1 | TIM8_CH1 |  |  | MDF1_CKI3 | LTDC_R0 | SDMMC1_D0DIR | TSC_G4_IO1 | DCMI_D0/PSSI_D0 | SDMMC2_D6 | SDMMC1_D6 | SAI2_MCLK_A |  | EVENTOUT
64 | PC7 | Output | GPIO_Output | SYS_RF_RED | PWR_CDSTOP |  | TIM3_CH2 | TIM8_CH2 |  |  | MDF1_SDI3 | LTDC_R1 | SDMMC1_D123DIR | TSC_G4_IO2 | DCMI_D1/PSSI_D1 | SDMMC2_D7 | SDMMC1_D7 | SAI2_MCLK_B | LPTIM2_CH2 | EVENTOUT
65 | PC8 | I/O | SDMMC1_D0 | SDIO_D0 | PWR_SRDSTOP |  | TIM3_CH3 | TIM8_CH3 |  |  |  | USART6_RX | LTDC_G0 | TSC_G4_IO3 | DCMI_D2/PSSI_D2 |  | SDMMC1_D0 |  | LPTIM3_CH1 | EVENTOUT
66 | PC9 | I/O | SDMMC1_D1 | SDIO_D1 | DEBUG_TRACED0 | TIM8_BKIN2 | TIM3_CH4 | TIM8_CH4 | DCMI_D3/PSSI_D3 |  |  | USART6_TX | LTDC_G1 | TSC_G4_IO4 |  |  | SDMMC1_D1 |  | LPTIM3_CH2 | EVENTOUT
67 | PA8 | I/O | RCC_MCO |  | RCC_MCO | TIM1_CH1 | GFXTIM_LCKCAL | SAI1_CK2 |  | SPI1_RDY |  | USART1_CK | SDMMC2_D1 |  | USB_OTG_HS_SOF | GFXTIM_FCKCAL | DEBUG_TRACECLK | SAI1_SCK_A | LPTIM2_CH1 | EVENTOUT
68 | PA9 | I/O | USB_OTG_HS_VBUS | USB_VBUS |  | TIM1_CH2 |  | SPI2_SCK |  | DCMI_D0/PSSI_D0 |  | USART1_TX |  |  |  |  |  | SAI1_FS_A | TIM15_BKIN | EVENTOUT
69 | PA10 | Input | GPIO_Input | SD_SW | CRS_SYNC | TIM1_CH3 | LPTIM2_IN2 | SAI1_D1 |  | DCMI_D1/PSSI_D1 |  | USART1_RX |  |  | USB_OTG_HS_ID |  |  | SAI1_SD_A | TIM17_BKIN | EVENTOUT
70 | PA11 | I/O | USB_OTG_HS_DM | USB_DM |  | TIM1_CH4 | TIM1_BKIN2 |  |  | SPI1_MISO |  | USART1_CTS |  | FDCAN1_RX |  |  |  |  |  | EVENTOUT
71 | PA12 | I/O | USB_OTG_HS_DP | USB_DP |  | TIM1_ETR |  |  |  | SPI1_MOSI | OCTOSPIM_P2_NCS | USART1_DE/USART1_RTS |  | FDCAN1_TX |  |  |  |  |  | EVENTOUT
72 | PA13 (JTMS/SWDIO) | I/O | DEBUG_JTMS-SWDIO | TRACE_SWDIO | DEBUG_JTMS-SWDIO | IR_OUT |  |  |  |  |  |  |  |  |  |  |  | SAI1_SD_B |  | EVENTOUT
73 | VDDUSB | Power
74 | VSS | Power
75 | VDD | Power
76 | PA14 (JTCK/SWCLK) | I/O | DEBUG_JTCK-SWCLK | TRACE_SWCLK | DEBUG_JTCK-SWCLK | LPTIM1_CH1 |  |  | I2C1_SMBA | I2C4_SMBA |  |  |  |  | USB_OTG_HS_SOF |  |  | SAI1_FS_B |  | EVENTOUT
77 | PA15 (JTDI) | I/O | USART2_RX | MBUS_RX_STM_RX | DEBUG_JTDI | TIM2_CH1 | TIM2_ETR | USART2_RX |  | SPI1_NSS | SPI3_NSS | USART3_DE/USART3_RTS | UART4_DE/UART4_RTS |  |  |  |  | SAI2_FS_B |  | EVENTOUT
78 | PC10 | I/O | SDMMC1_D2 | SDIO_D2 | DEBUG_TRACED1 |  | LPTIM3_ETR | ADF1_CCK1 |  |  | SPI3_SCK | USART3_TX | UART4_TX | TSC_G3_IO2 | DCMI_D8/PSSI_D8 |  | SDMMC1_D2 | SAI2_SCK_B |  | EVENTOUT
79 | PC11 | I/O | SDMMC1_D3 | SDIO_D3 |  |  | LPTIM3_IN1 | ADF1_SDI0 | DCMI_D2/PSSI_D2 | OCTOSPIM_P1_NCS | SPI3_MISO | USART3_RX | UART4_RX | TSC_G3_IO3 | DCMI_D4/PSSI_D4 | UCPD1_FRSTX2 | SDMMC1_D3 | SAI2_MCLK_B |  | EVENTOUT
80 | PC12 | I/O | SDMMC1_CK | SDIO_CLK | DEBUG_TRACED3 |  |  |  |  |  | SPI3_MOSI | USART3_CK | UART5_TX | TSC_G3_IO4 | DCMI_D9/PSSI_D9 |  | SDMMC1_CK | SAI2_SD_B |  | EVENTOUT
81 | PD0 | I/O | I2C5_SDA | SENS_I2C_SDA |  |  | I2C6_SDA | TIM8_CH4N | I2C5_SDA | SPI2_NSS |  |  | LTDC_B4 | FDCAN1_RX |  |  | FMC_D2/FMC_DA2 |  |  | EVENTOUT
82 | PD1 | I/O | I2C5_SCL | SENS_I2C_SCL |  |  | I2C6_SCL |  | I2C5_SCL | SPI2_SCK |  |  | LTDC_B5 | FDCAN1_TX |  |  | FMC_D3/FMC_DA3 |  |  | EVENTOUT
83 | PD2 | I/O | SDMMC1_CMD | SDIO_CMD | DEBUG_TRACED2 |  | TIM3_ETR |  | I2C5_SMBA |  |  | USART3_DE/USART3_RTS | UART5_RX | TSC_SYNC | DCMI_D11/PSSI_D11 |  | SDMMC1_CMD | LPTIM4_ETR | FMC_A20 | EVENTOUT
84 | PD3 | I/O | MDF1_SDI0 | MIC_SD0 |  |  | I2C6_SMBA | SPI2_SCK | DCMI_D5/PSSI_D5 | SPI2_MISO | MDF1_SDI0 | USART2_CTS | LTDC_CLK |  | OCTOSPIM_P2_NCS |  | FMC_CLK |  |  | EVENTOUT
85 | PD4 | Output | GPIO_Output | SYS_SD_BLUE |  |  |  |  |  | SPI2_MOSI | MDF1_CKI0 | USART2_DE/USART2_RTS |  |  | OCTOSPIM_P1_IO4 |  | FMC_NOE |  |  | EVENTOUT
86 | PD5 | I/O | USART2_TX | MBUS_TX_STM_TX |  |  |  |  |  | SPI2_RDY |  | USART2_TX |  |  | OCTOSPIM_P1_IO5 |  | FMC_NWE |  |  | EVENTOUT
87 | PD6 | I/O | MDF1_SDI1 | MIC_SD1 |  |  |  | SAI1_D1 | DCMI_D10/PSSI_D10 | SPI3_MOSI | MDF1_SDI1 | USART2_RX | LTDC_DE |  | OCTOSPIM_P1_IO6 | SDMMC2_CK | FMC_NWAIT | SAI1_SD_A |  | EVENTOUT
88 | PD7 | Output | GPIO_Output | SD_PWR |  |  | GFXTIM_FCKCAL |  |  | GFXTIM_LCKCAL | MDF1_CKI1 | USART2_CK |  |  | OCTOSPIM_P1_IO7 | SDMMC2_CMD | FMC_NCE/FMC_NE1 | LPTIM4_OUT |  | EVENTOUT
89 | PB3 (JTDO/TRACESWO) | I/O | DEBUG_JTDO-SWO | TRACE_SWO | DEBUG_JTDO-SWO | TIM2_CH2 | LPTIM1_CH1 | ADF1_CCK0 | I2C1_SDA | SPI1_SCK | SPI3_SCK | USART1_DE/USART1_RTS |  |  | CRS_SYNC |  | SDMMC2_D2 | SAI1_SCK_B |  | EVENTOUT
90 | PB4 (NJTRST) | Output | GPIO_Output | EXT_3 | DEBUG_JTRST | LPTIM1_CH2 | TIM3_CH1 | ADF1_SDI0 | I2C3_SDA | SPI1_MISO | SPI3_MISO | USART1_CTS | UART5_DE/UART5_RTS | TSC_G2_IO1 | DCMI_D12/PSSI_D12 |  | SDMMC2_D3 | SAI1_MCLK_B | TIM17_BKIN | EVENTOUT
91 | PB5 | Output | GPIO_Output | SYS_MAIN_RED |  | LPTIM1_IN1 | TIM3_CH2 | OCTOSPIM_P1_NCLK | I2C1_SMBA | SPI1_MOSI | SPI3_MOSI | USART1_CK | UART5_CTS | TSC_G2_IO2 | DCMI_D10/PSSI_D10 |  | COMP2_OUT | SAI1_SD_B | TIM16_BKIN | EVENTOUT
92 | PB6 | I/O | I2C1_SCL | EXT_I2C_SCL |  | LPTIM1_ETR | TIM4_CH1 | TIM8_BKIN2 | I2C1_SCL | I2C4_SCL | MDF1_SDI5 | USART1_TX |  | TSC_G2_IO3 | DCMI_D5/PSSI_D5 |  |  | SAI1_FS_B | TIM16_CH1N | EVENTOUT
93 | PB7 | I/O | I2C1_SDA | EXT_I2C_SDA |  | LPTIM1_IN2 | TIM4_CH2 | TIM8_BKIN | I2C1_SDA | I2C4_SDA | MDF1_CKI5 | USART1_RX | UART4_CTS | TSC_G2_IO4 | DCMI_VSYNC/PSSI_RDY | GFXTIM_TE | FMC_NL |  | TIM17_CH1N | EVENTOUT
94 | PH3-BOOT0 | Input | GPIO_Input | BOOT0 |  |  |  |  |  |  |  |  |  |  |  |  |  |  |  | EVENTOUT
95 | PB8 | Output | GPIO_Output | EXT_2 |  |  | TIM4_CH3 | SAI1_CK1 | I2C1_SCL | MDF1_CCK0 | SPI3_RDY | LTDC_B1 | SDMMC1_CKIN | FDCAN1_RX | DCMI_D6/PSSI_D6 | SDMMC2_D4 | SDMMC1_D4 | SAI1_MCLK_A | TIM16_CH1 | EVENTOUT
96 | PB9 | Output | GPIO_Output | EXT_1 |  | IR_OUT | TIM4_CH4 | SAI1_D2 | I2C1_SDA | SPI2_NSS |  | LTDC_B0 | SDMMC1_CDIR | FDCAN1_TX | DCMI_D7/PSSI_D7 | SDMMC2_D5 | SDMMC1_D5 | SAI1_FS_A | TIM17_CH1 | EVENTOUT
97 | PE0 | Input | GPIO_Input | CHG_INT |  |  | TIM4_ETR |  |  |  |  | USART6_RX | LTDC_HSYNC |  | DCMI_D2/PSSI_D2 |  | FMC_NBL0 |  | TIM16_CH1 | EVENTOUT
98 | VDD11 | Power
99 | VSS | Power
100 | VDD | Power

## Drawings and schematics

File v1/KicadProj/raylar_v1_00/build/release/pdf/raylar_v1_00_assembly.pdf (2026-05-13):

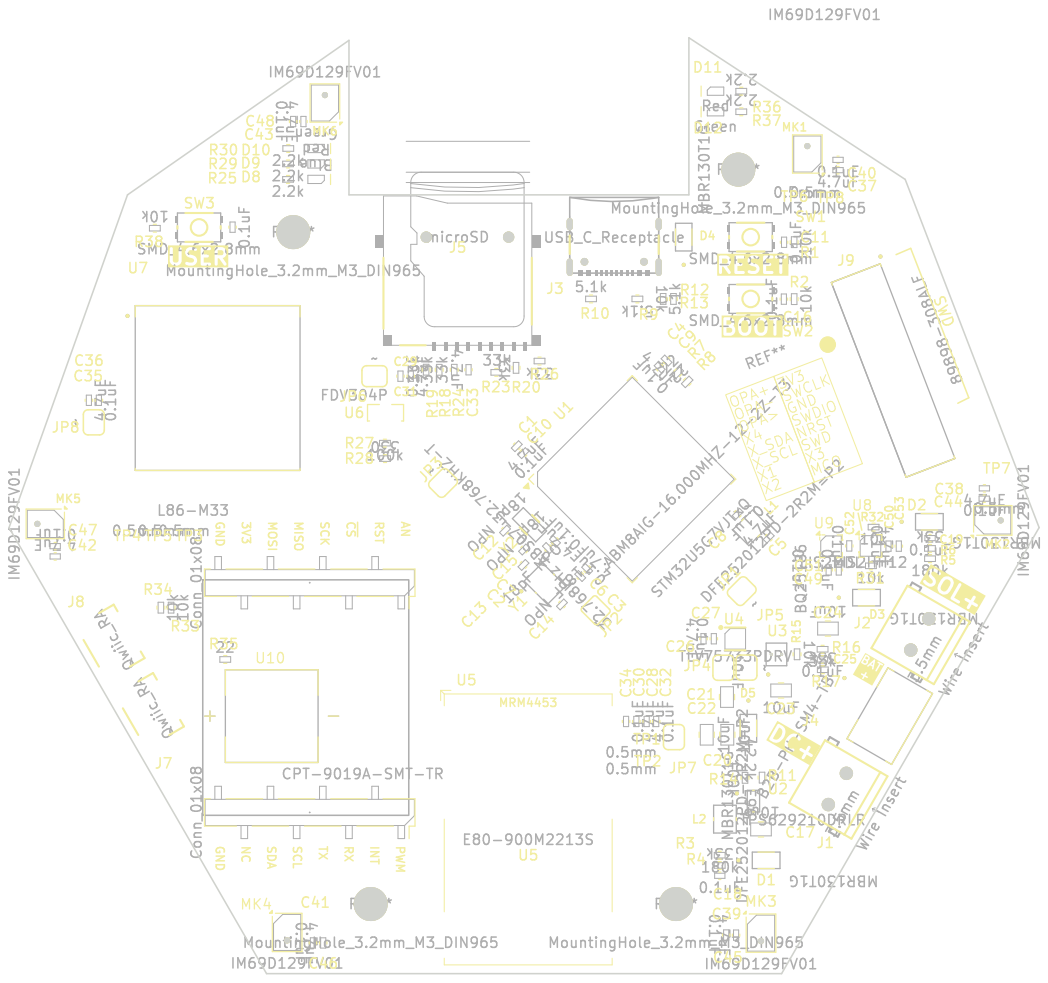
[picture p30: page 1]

NPO 0.1uF33k DFE252012PD-2R2M=P2 GND MISO AN SWD TXRX MOSI ~{CS} NCSDA SCL INT PWM GND RST MRM4453 3V3 SCK TP2 R18 R16 R28 C7 D8 R33 R27 R20

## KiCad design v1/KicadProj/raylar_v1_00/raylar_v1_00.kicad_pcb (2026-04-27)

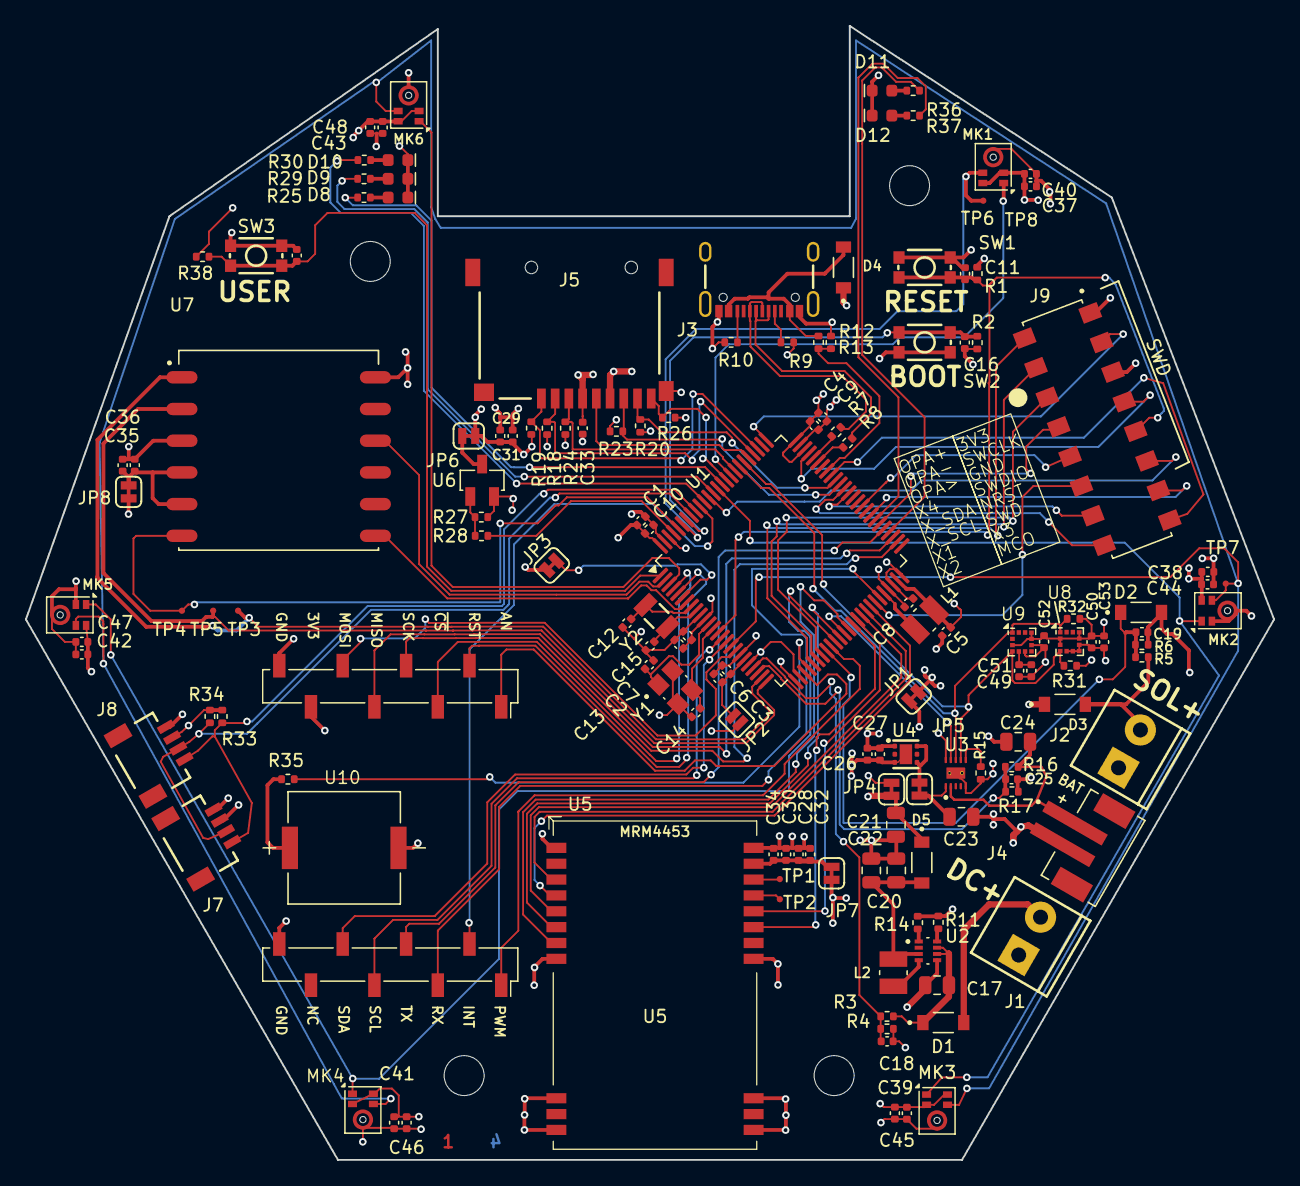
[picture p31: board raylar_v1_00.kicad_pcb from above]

Board: 4 copper layers, 100.0 x 90.9 mm, 149 parts (0 on the bottom side), 114 nets.

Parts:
C1, C2, C4, C5, C6, C26, C28, C30, C31, C33, C35, C37, C38, C39, C41, C42, C43, C53: 4.7uF; C_0402_1005Metric
C3, C7, C8, C9, C10, C11, C16, C18, C19, C25, C27, C29, C32, C34, C36, C40, C44, C45, C46, C47, C48, C49, C50, C51, C52, C54: 0.1uF; C_0402_1005Metric
C12, C13, C14, C15: 18pF NPO; C_0402_1005Metric
C17, C20, C21, C22, C23, C24: 10uF; C_0805_2012Metric
D1, D2, D3, D4, D5: MBR130T1G; DIO_MBR0530T1G
D8: Blue; LED_0603_1608Metric_Blue
D9, D11: Red; LED_0603_1608Metric_Red
D10, D12: Green; LED_0603_1608Metric_Green
J1, J2: 3.5mm; ScrewTerminal_1x02_P3.5mm_Horizontal_Black
J3: USB_C_Receptacle; USB-C_16
J4: B2B-PH-SM4-TB; JST_B2B-PH-SM4-TB
J5: microSD; microSD_External_Pin
J6, J10: Conn_01x08; 1x08_P2.54mm_Socket_Vertical_SMD_Pin1RightDown
J7, J8: Qwiic_RA; JST_1x04_P1.0mm_Horizontal_SMD
J9: 89898-308ALF; AMPHENOL_89898-308ALF
JP1, JP3, JP4, JP5, JP6, JP7, JP8: Jumper_2_NC_Trace
JP2: Jumper_2_NO
L1, L2: DFE252012PD-2R2M=P2; INDC2520X120N
MK1, MK2, MK3, MK4, MK5, MK6: IM69D129FV01; Knowles_LGA-5_3.5x2.65mm
R1, R2, R13, R15, R31, R32, R33, R34, R38: 10k; R_0402_1005Metric
R3, R5: 180k; R_0402_1005Metric
R4, R6, R16, R17, R18, R19, R20, R23, R24, R26: 33k; R_0402_1005Metric
R7, R8, R35: 22; R_0402_1005Metric
R9, R10, R12: 5.1k; R_0402_1005Metric
R11: 42.2k E96; R_0402_1005Metric
R14, R27: 100k; R_0402_1005Metric
R25, R29, R30, R36, R37: 2.2k; R_0402_1005Metric
R28: 330; R_0402_1005Metric
SW1, SW2, SW3: SMD_4.6x2.8mm; Push_SMD_4.6x2.8mm_h1.9mm
TP1, TP2, TP3, TP4, TP5, TP6, TP7, TP8: 0.5mm; TestPoint-0.5mm
U1: STM32U5G7VJTxQ; LQFP-100_14x14mm_P0.5mm
U2: TPS629210DRLR; SOT50P160X60-8N
U3: BQ25186; IC_BQ25185DLHR
U4: TLV75733PDRV; WDFN-6_2x2mm
U5: E80-900M2213S; E80-x00M2213S
U6: FDV304P; SOT23-3
U7: L86-M33; XCVR_L86-M33
U8: LIS2HH12; LGA-12_2x2mm_P0.5mm
U9: LIS2MDL; LGA-12_2x2mm_P0.5mm
U10: CPT-9019A-SMT-TR; XDCR_CPT-9019A-SMT-TR
Y1: ABM8AIG-16.000MHZ-12-2Z-T3; XTAL_ABM8AIG-16.000MHZ-12-2Z-T3
Y2: 32.768kHz ABS07-32.768KHZ-T; Crystal_SMD_3.2x1.5mm

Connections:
3.3V: C26.1, C27.1, C37.1, C38.1, C39.1, C40.1, C41.1, C42.1, C43.1, C44.1, C45.1, C46.1, C47.1, C48.1, C50.1, C52.1, C53.1, J6.7, J7.2, J8.2, J9.01, JP1.1 (A), JP7.2 (B), JP8.2 (B), MK1.2 (SEL), MK1.5 (VDD), MK2.5 (VDD), MK3.2 (SEL), MK3.5 (VDD), MK4.2 (SEL), MK4.5 (VDD), MK5.5 (VDD), MK6.2 (SEL), MK6.5 (VDD), R1.2, R27.2, R31.2, R32.2, R33.2, R34.2, R38.2, SW2.2, U4.1 (OUT), U6.2, U8.2 (~CS), U8.3 (SA0/SDO), U8.9 (Vdd), U8.10 (Vdd_IO), U9.3 (~CS), U9.9 (Vdd), U9.10 (Vdd_IO)
32K_OSC_IN: C12.1, U1.8 (PC14), Y2.1
32K_OSC_OUT: C15.1, U1.9 (PC15), Y2.2
/Sheet2/USB_DIFF_N: J3.A7 (D-), J3.B7 (D-), R8.1
/Sheet2/USB_DIFF_P: J3.A6 (D+), J3.B6 (D+), R7.1
BOOT0: C16.1, R2.2, SW2.1, U1.94 (PH3)
CHG_INT: U1.37 (PE9), U3.9 (/INT)
EXT_1: J9.14, U1.63 (PC6)
EXT_2: J9.16, U1.64 (PC7)
EXT_3: J9.13, U1.58 (PD11)
EXT_AN_IN: J9.08, U1.56 (PD9)
EXT_I2C_SCL: J9.12, U1.44 (PB10)
EXT_I2C_SDA: J9.10, U1.60 (PD13)
EXT_OPA_VINM: J9.04, U1.31 (PA7)
EXT_OPA_VINP: J9.02, U1.30 (PA6)
EXT_OPA_VOUT: J9.06, U1.32 (PB0)
GND: C1.2, C2.2, C3.2, C4.2, C5.2, C6.2, C7.2, C8.2, C9.2, C10.2, C11.2, C12.2, C13.2, C14.2, C15.2, C16.2, C17.2, C18.2, C19.2, C20.2, C21.2, C22.2, C23.2, C24.2, C25.2, C26.2, C27.2, C28.2, C29.2, C30.2, C31.2, C32.2, C33.2, C34.2, C35.2, C36.2, C37.2, C38.2, C39.2, C40.2, C41.2, C42.2, C43.2, C44.2, C45.2, C46.2, C47.2, C48.2, C49.2, C50.2, C51.2, C52.2, C53.2, C54.2, D2.A, D8.1 (K), D9.1 (K), D10.1 (K), D11.1 (K), D12.1 (K), J1.1, J2.1, J3.GND, J3.S (SHIELD), J4.2, J5.6 (VSS), J5.10 (SHIELD), J6.8, J7.1, J8.1, J9.05, J10.8, MK1.3 (GND), MK2.2 (SEL), MK2.3 (GND), MK3.3 (GND), MK4.3 (GND), MK5.2 (SEL), MK5.3 (GND), MK6.3 (GND), R2.1, R4.1, R6.1, R9.2, R10.2, R11.1, R13.1, R14.1, R15.1, R17.1, SW1.1, SW3.1, U1.10 (VSS), U1.19 (VSSA), U1.26 (VSS), U1.48 (VSSSMPS), U1.50 (VSS), U1.74 (VSS), U1.99 (VSS), U2.5 (GND), U3.5 (GND), U3.11 (GND_(THERMAL)), U4.3 (GND), U4.7 (GND), U5.1 (GND), U5.8 (GND), U5.11 (GND), U5.13 (GND), U5.14 (GND), U5.16 (GND), U5.19 (GND), U5.26 (GND), U7.3 (GND), U7.12 (GND), U8.5 (RES), U8.6 (GND), U8.7 (GND), U8.8 (GND), U9.6 (GND), U9.8 (GND), U10.N, Y1.2 (GND), Y1.4 (GND)
GPS_EN: U1.7 (PC13), U7.7 (FORCE_ON)
GPS_PPS: TP4.1, U1.96 (PB9), U7.6 (1PPS)
GPS_RESET: U1.2 (PE3), U7.10 (~RESET)
GPS_RX_STM_TX: TP3.1, U1.24 (PA2), U7.1 (RXD1)
GPS_TX_STM_RX: TP5.1, U1.25 (PA3), U7.2 (TXD1)
HSE_OSC_IN: C13.1, U1.12 (PH0), Y1.1
HSE_OSC_OUT: C14.1, U1.13 (PH1), Y1.3
MBUS_AN: J6.1, U1.28 (PA4)
MBUS_CS: J6.3, U1.4 (PE5)
MBUS_INT: J10.2, U1.91 (PB5)
MBUS_MISO: J6.5, U1.53 (PB14)
MBUS_MOSI: J6.6, U1.18 (PC3)
MBUS_PWM: J10.1, U1.34 (PB2)
MBUS_RST: J6.2, U1.5 (PE6)
MBUS_RX_STM_RX: J10.3, U1.45 (PB11)
MBUS_SCK: J6.4, U1.52 (PB13)
MBUS_SCL: J10.5, U1.15 (PC0)
MBUS_SDA: J10.6, U1.16 (PC1)
MBUS_TX_STM_TX: J10.4, U1.55 (PD8)
MIC_CCLK0: MK1.4 (CLOCK), TP6.1, U1.95 (PB8)
MIC_CCLK1: MK2.4 (CLOCK), MK3.4 (CLOCK), MK4.4 (CLOCK), MK5.4 (CLOCK), MK6.4 (CLOCK), TP7.1, U1.17 (PC2)
MIC_SD0: MK1.1 (DATA), TP8.1, U1.84 (PD3)
MIC_SD1: MK2.1 (DATA), MK3.1 (DATA), U1.87 (PD6)
MIC_SD2: MK4.1 (DATA), MK5.1 (DATA), U1.35 (PE7)
MIC_SD3: MK6.1 (DATA), U1.3 (PE4)
NRST: C11.1, J9.09, R1.1, SW1.2, U1.14 (NRST)
unnamed: C5.1, L1.2, U1.49 (VDD11), U1.98 (VDD11)
unnamed: D4.A, J3.VBUS, R12.2
unnamed: D8.2 (A), R25.2
unnamed: D9.2 (A), R29.2
unnamed: D10.2 (A), R30.2
unnamed: D11.2 (A), R36.2
unnamed: D12.2 (A), R37.2
unnamed: D1.A, J1.2
unnamed: D3.A, J2.2, R5.2
unnamed: J3.A5 (CC1), R9.1
unnamed: J3.B5 (CC2), R10.1
unnamed: C3.1, C6.1, JP2.2 (B), U1.20 (VREF+)
unnamed: JP3.1 (A), U1.6 (VBAT)
unnamed: C21.1, D3.C, D4.C, D5.C, JP4.1 (A)
unnamed: JP4.2 (B), U3.10 (IN)
unnamed: C23.1, JP5.1 (A), U3.1 (SYS)
unnamed: JP5.2 (B), U4.4 (EN), U4.6 (IN)
unnamed: JP6.2 (B), U6.3
unnamed: R27.1, R28.2, U6.1
unnamed: R35.2, U10.P
unnamed: L1.1, U1.46 (VLXSMPS)
unnamed: C17.1, D1.C, R3.2, U2.6 (VIN), U2.7 (EN)
unnamed: R14.2, U2.1 (FB/VSET)
unnamed: R11.2, U2.8 (MODE/S-CONF)
unnamed: L2.1, U2.4 (SW)
unnamed: C20.1, C22.1, D5.A, L2.2, U2.3 (VOS)
unnamed: C24.1, J4.1, R16.2, U3.2 (BAT)
unnamed: R15.2, U3.6 (TS/MR)
unnamed: TP1.1, U5.24 (DIO7)
unnamed: TP2.1, U5.23 (DIO8)
unnamed: C49.1, C51.1, U9.5 (C1)
PWM_BUZ: R35.1, U1.29 (PA5)
QWIIC_SCL: J7.4, J8.4, R33.1, U1.92 (PB6)
QWIIC_SDA: J7.3, J8.3, R34.1, U1.93 (PB7)
RCC_MCO: J9.15, U1.67 (PA8)
RF_BUSY: U1.38 (PE10), U5.7 (BUSY)
RF_CS: U1.36 (PE8), U5.6 (NSS)
RF_IRQ: U1.40 (PE12), U5.22 (DIO9/IRQ)
RF_MISO: U1.42 (PE14), U5.3 (MISO)
RF_MOSI: U1.43 (PE15), U5.4 (MOSI)
RF_NRST: U1.39 (PE11), U5.21 (LR_NRESET)
RF_SCK: U1.41 (PE13), U5.5 (SCK)
SDIO_CLK: J5.5 (CLK/SCK), U1.80 (PC12)
SDIO_CMD: J5.3 (CMD/SDI), R24.1, U1.83 (PD2)
SDIO_D0: J5.7 (DAT0/SDO), R23.1, U1.65 (PC8)
SDIO_D1: J5.8 (DAT1), R20.1, U1.66 (PC9)
SDIO_D2: J5.1 (DAT2), R19.1, U1.78 (PC10)
SDIO_D3: J5.2 (DAT3/CD), R18.1, U1.79 (PC11)
SD_PWR: R28.1, U1.97 (PE0)
SD_SW: J5.9 (~DET), R26.1, U1.85 (PD4)
SENS_I2C_SCL: R32.1, U1.82 (PD1), U3.8 (SCL), U8.1 (SCL/SPC), U9.1 (SCL/SPC)
SENS_I2C_SDA: R31.1, U1.81 (PD0), U3.7 (SDA), U8.4 (SDA/SDI), U9.4 (SDA/SDI/SDO)
SW_USER: C54.1, R38.1, SW3.2, U1.1 (PE2)
SYS_GPS_GREEN: R30.1, U1.90 (PB4)
SYS_GPS_RED: R29.1, U1.88 (PD7)
SYS_MAIN_GREEN: R37.1, U1.57 (PD10)
SYS_MAIN_RED: R36.1, U1.54 (PB15)
SYS_SD_BLUE: R25.1, U1.86 (PD5)
TRACE_SWCLK: J9.03, U1.76 (PA14)
TRACE_SWDIO: J9.07, U1.72 (PA13)
TRACE_SWO: J9.11, U1.89 (PB3)
USB_D_N: R8.2, U1.70 (PA11)
USB_D_P: R7.2, U1.71 (PA12)
USB_VBUS: R12.1, R13.2, U1.68 (PA9)
VCC_GPS: C35.1, C36.1, JP8.1 (A), U7.4 (VCC), U7.5 (V_BCKP)
VCC_RF: C28.1, C30.1, C32.1, C34.1, JP7.1 (A), U5.25 (VCC)
VCC_SD: C29.1, C31.1, C33.1, J5.4 (VDD), JP6.1 (A), R18.2, R19.2, R20.2, R23.2, R24.2, R26.2
VDD_MCU: C1.1, C2.1, C4.1, C7.1, C8.1, C9.1, C10.1, JP1.2 (B), JP2.1 (A), JP3.2 (B), U1.11 (VDD), U1.21 (VDDA), U1.27 (VDD), U1.47 (VDDSMPS), U1.73 (VDDUSB), U1.75 (VDD), U1.100 (VDD)
V_ADC_BATT: C25.1, R16.1, R17.2, U1.23 (PA1)
V_ADC_DC: C18.1, R3.1, R4.2, U1.22 (PA0)
V_ADC_SOLAR: C19.1, D2.C, R5.1, R6.2, U1.33 (PB1)

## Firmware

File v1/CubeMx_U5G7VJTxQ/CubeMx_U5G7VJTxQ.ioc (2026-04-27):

#MicroXplorer Configuration settings - do not modify
ADC2.Channel-0\#ChannelRegularConversion=ADC_CHANNEL_6
ADC2.IPParameters=Rank-0\#ChannelRegularConversion,Channel-0\#ChannelRegularConversion,SamplingTime-0\#ChannelRegularConversion,OffsetNumber-0\#ChannelRegularConversion,MonitoredBy-0\#ChannelRegularConversion,NbrOfConversionFlag
ADC2.MonitoredBy-0\#ChannelRegularConversion=__NULL
ADC2.NbrOfConversionFlag=1
ADC2.OffsetNumber-0\#ChannelRegularConversion=ADC_OFFSET_NONE
ADC2.Rank-0\#ChannelRegularConversion=1
ADC2.SamplingTime-0\#ChannelRegularConversion=ADC_SAMPLETIME_5CYCLE
CAD.formats=
CAD.pinconfig=
CAD.provider=
CORTEX_M33_NS.userName=CORTEX_M33
File.Version=6
GPIO.groupedBy=
I2C1.IPParameters=Timing
I2C1.Timing=0x10707DBC
I2C3.IPParameters=Timing
I2C3.Timing=0x10707DBC
I2C4.IPParameters=Timing
I2C4.Timing=0x10707DBC
I2C5.IPParameters=Timing
I2C5.Timing=0x10707DBC
KeepUserPlacement=true
MMTAppRegionsCount=0
MMTConfigApplied=false
Mcu.CPN=STM32U5G7VJT6Q
Mcu.ContextProject=TrustZoneDisabled
Mcu.Family=STM32U5
Mcu.IP0=ADC2
Mcu.IP1=CORTEX_M33_NS
Mcu.IP10=MEMORYMAP
Mcu.IP11=NVIC
Mcu.IP12=OPAMP2
Mcu.IP13=PWR
Mcu.IP14=RCC
Mcu.IP15=RTC
Mcu.IP16=SDMMC1
Mcu.IP17=SPI1
Mcu.IP18=SPI2
Mcu.IP19=SYS
Mcu.IP2=DEBUG
Mcu.IP20=TIM4
Mcu.IP21=TIM8
Mcu.IP22=TIM17
Mcu.IP23=USART2
Mcu.IP24=USART3
Mcu.IP25=USB_OTG_HS
Mcu.IP26=VREFBUF
Mcu.IP3=I2C1
Mcu.IP4=I2C3
Mcu.IP5=I2C4
Mcu.IP6=I2C5
Mcu.IP7=LPBAM
Mcu.IP8=LPBAMQUEUE
Mcu.IP9=MDF1
Mcu.IPNb=27
Mcu.Name=STM32U5G7VJTxQ
Mcu.Package=LQFP100
Mcu.Pin0=PE2
Mcu.Pin1=PE3
Mcu.Pin10=PC0
Mcu.Pin11=PC1
Mcu.Pin12=PC2
Mcu.Pin13=PC3
Mcu.Pin14=VREF+
Mcu.Pin15=PA0
Mcu.Pin16=PA1
Mcu.Pin17=PA2
Mcu.Pin18=PA3
Mcu.Pin19=PA4
Mcu.Pin2=PE4
Mcu.Pin20=PA5
Mcu.Pin21=PA6
Mcu.Pin22=PA7
Mcu.Pin23=PB0
Mcu.Pin24=PB1
Mcu.Pin25=PB2
Mcu.Pin26=PE7
Mcu.Pin27=PE8
Mcu.Pin28=PE10
Mcu.Pin29=PE11
Mcu.Pin3=PE5
Mcu.Pin30=PE12
Mcu.Pin31=PE13
Mcu.Pin32=PE14
Mcu.Pin33=PE15
Mcu.Pin34=PB10
Mcu.Pin35=PB11
Mcu.Pin36=PB13
Mcu.Pin37=PB14
Mcu.Pin38=PD8
Mcu.Pin39=PD12
Mcu.Pin4=PE6
Mcu.Pin40=PD13
Mcu.Pin41=PD14
Mcu.Pin42=PD15
Mcu.Pin43=PC6
Mcu.Pin44=PC7
Mcu.Pin45=PC8
Mcu.Pin46=PC9
Mcu.Pin47=PA8
Mcu.Pin48=PA9
Mcu.Pin49=PA11
Mcu.Pin5=PC13
Mcu.Pin50=PA12
Mcu.Pin51=PA13 (JTMS/SWDIO)
Mcu.Pin52=PA14 (JTCK/SWCLK)
Mcu.Pin53=PC10
Mcu.Pin54=PC11
Mcu.Pin55=PC12
Mcu.Pin56=PD0
Mcu.Pin57=PD1
Mcu.Pin58=PD2
Mcu.Pin59=PD3
Mcu.Pin6=PC14-OSC32_IN (PC14)
Mcu.Pin60=PD4
Mcu.Pin61=PD6
Mcu.Pin62=PB3 (JTDO/TRACESWO)
Mcu.Pin63=PB4 (NJTRST)
Mcu.Pin64=PB5
Mcu.Pin65=PB6
Mcu.Pin66=PB7
Mcu.Pin67=PH3-BOOT0
Mcu.Pin68=PB8
Mcu.Pin69=PB9
Mcu.Pin7=PC15-OSC32_OUT (PC15)
Mcu.Pin70=PE0
Mcu.Pin71=VP_LPBAMQUEUE_VS_QUEUE
Mcu.Pin72=VP_MDF1_VS_MDF_DFLT0
Mcu.Pin73=VP_MDF1_VS_MDF_DFLT1
Mcu.Pin74=VP_MDF1_VS_MDF_DFLT2
Mcu.Pin75=VP_MDF1_VS_MDF_DFLT3
Mcu.Pin76=VP_PWR_VS_SECSignals
Mcu.Pin77=VP_PWR_VS_LPOM
Mcu.Pin78=VP_PWR_Vdda
Mcu.Pin79=VP_RTC_VS_RTC_Activate
Mcu.Pin8=PH0-OSC_IN (PH0)
Mcu.Pin80=VP_SYS_VS_Systick
Mcu.Pin81=VP_TIM17_VS_ClockSourceINT
Mcu.Pin82=VP_TIM17_VS_NoInput1
Mcu.Pin83=VP_LPBAM_VS_SIG1
Mcu.Pin84=VP_LPBAM_VS_SIG4
Mcu.Pin85=VP_MEMORYMAP_VS_MEMORYMAP
Mcu.Pin9=PH1-OSC_OUT (PH1)
Mcu.PinsNb=86
Mcu.ThirdPartyNb=0
Mcu.UserConstants=
Mcu.UserName=STM32U5G7VJTxQ
MxCube.Version=6.12.0
MxDb.Version=DB.6.0.120
NVIC.BusFault_IRQn=true\:0\:0\:false\:false\:true\:false\:false\:false
NVIC.DebugMonitor_IRQn=true\:0\:0\:false\:false\:true\:false\:false\:false
NVIC.ForceEnableDMAVector=true
NVIC.HardFault_IRQn=true\:0\:0\:false\:false\:true\:false\:false\:false
NVIC.MemoryManagement_IRQn=true\:0\:0\:false\:false\:true\:false\:false\:false
NVIC.NonMaskableInt_IRQn=true\:0\:0\:false\:false\:true\:false\:false\:false
NVIC.PendSV_IRQn=true\:0\:0\:false\:false\:true\:false\:false\:false
NVIC.PriorityGroup=NVIC_PRIORITYGROUP_4
NVIC.SVCall_IRQn=true\:0\:0\:false\:false\:true\:false\:false\:false
NVIC.SysTick_IRQn=true\:15\:0\:false\:false\:true\:false\:true\:false
NVIC.UsageFault_IRQn=true\:0\:0\:false\:false\:true\:false\:false\:false
PA0.Mode=IN5-Single-Ended
PA0.Signal=ADC2_IN5
PA1.Mode=IN6-Single-Ended
PA1.Signal=ADC2_IN6
PA11.GPIOParameters=GPIO_Label
PA11.GPIO_Label=USB_DM
PA11.Mode=Internal_Phy_Device
PA11.Signal=USB_OTG_HS_DM
PA12.GPIOParameters=GPIO_Label
PA12.GPIO_Label=USB_DP
PA12.Mode=Internal_Phy_Device
PA12.Signal=USB_OTG_HS_DP
PA13\ (JTMS/SWDIO).GPIOParameters=GPIO_Label
PA13\ (JTMS/SWDIO).GPIO_Label=TRACE_SWDIO
PA13\ (JTMS/SWDIO).Mode=Trace_Asynchronous_SW
PA13\ (JTMS/SWDIO).Signal=DEBUG_JTMS-SWDIO
PA14\ (JTCK/SWCLK).GPIOParameters=GPIO_Label
PA14\ (JTCK/SWCLK).GPIO_Label=TRACE_SWCLK
PA14\ (JTCK/SWCLK).Mode=Trace_Asynchronous_SW
PA14\ (JTCK/SWCLK).Signal=DEBUG_JTCK-SWCLK
PA2.GPIOParameters=GPIO_Label
PA2.GPIO_Label=GPS_RX_STM_TX
PA2.Locked=true
PA2.Mode=Asynchronous
PA2.Signal=USART2_TX
PA3.GPIOParameters=GPIO_Label
PA3.GPIO_Label=GPS_TX_STM_RX
PA3.Locked=true
PA3.Mode=Asynchronous
PA3.Signal=USART2_RX
PA4.GPIOParameters=GPIO_Label
PA4.GPIO_Label=MBUS_AN
PA4.Mode=IN9-Single-Ended
PA4.Signal=ADC2_IN9
PA5.GPIOParameters=GPIO_Label
PA5.GPIO_Label=BUZ
PA5.Locked=true
PA5.Signal=SharedStack_PA5
PA5.Stacked=true
PA6.GPIOParameters=GPIO_Label
PA6.GPIO_Label=EXT_OPA_VINP
PA6.Mode=Standalone
PA6.Signal=OPAMP2_VINP
PA7.GPIOParameters=GPIO_Label
PA7.GPIO_Label=EXT_OPA_VINM
PA7.Mode=Standalone
PA7.Signal=OPAMP2_VINM
PA8.Mode=Clock-out
PA8.Signal=RCC_MCO
PA9.GPIOParameters=GPIO_Label
PA9.GPIO_Label=USB_VBUS
PA9.Mode=Activate_VBUS_FS
PA9.Signal=USB_OTG_HS_VBUS
PB0.GPIOParameters=GPIO_Label
PB0.GPIO_Label=EXT_OPA_VOUT
PB0.Mode=Standalone
PB0.Signal=OPAMP2_VOUT
PB1.Mode=IN16-Single-Ended
PB1.Signal=ADC2_IN16
PB10.GPIOParameters=GPIO_Label
PB10.GPIO_Label=EXT_I2C_SCL
PB10.Locked=true
PB10.Mode=I2C
PB10.Signal=I2C4_SCL
PB11.GPIOParameters=GPIO_Label
PB11.GPIO_Label=MBUS_RX_STM_RX
PB11.Mode=Asynchronous
PB11.Signal=USART3_RX
PB13.GPIOParameters=GPIO_Label
PB13.GPIO_Label=MBUS_SCK
PB13.Mode=Full_Duplex_Master
PB13.Signal=SPI2_SCK
PB14.GPIOParameters=GPIO_Label
PB14.GPIO_Label=MBUS_MISO
PB14.Mode=Full_Duplex_Master
PB14.Signal=SPI2_MISO
PB2.GPIOParameters=GPIO_Label
PB2.GPIO_Label=MBUS_PWM
PB2.Locked=true
PB2.Mode=PWM Generation4 CH4N
PB2.Signal=TIM8_CH4N
PB3\ (JTDO/TRACESWO).GPIOParameters=GPIO_Label
PB3\ (JTDO/TRACESWO).GPIO_Label=TRACE_SWO
PB3\ (JTDO/TRACESWO).Mode=Trace_Asynchronous_SW
PB3\ (JTDO/TRACESWO).Signal=DEBUG_JTDO-SWO
PB4\ (NJTRST).GPIOParameters=GPIO_Label
PB4\ (NJTRST).GPIO_Label=EXT_3
PB4\ (NJTRST).Locked=true
PB4\ (NJTRST).Signal=GPIO_Output
PB5.GPIOParameters=GPIO_Label
PB5.GPIO_Label=SYS_MAIN_RED
PB5.Locked=true
PB5.Signal=GPIO_Output
PB6.GPIOParameters=GPIO_Label
PB6.GPIO_Label=QWIIC_SCL
PB6.Locked=true
PB6.Mode=I2C
PB6.Signal=I2C1_SCL
PB7.GPIOParameters=GPIO_Label
PB7.GPIO_Label=QWIIC_SDA
PB7.Locked=true
PB7.Mode=I2C
PB7.Signal=I2C1_SDA
PB8.GPIOParameters=GPIO_Label
PB8.GPIO_Label=MIC_CCLK0
PB8.Locked=true
PB8.Mode=MOD_MDF_CCK0
PB8.Signal=MDF1_CCK0
PB9.GPIOParameters=GPIO_Label
PB9.GPIO_Label=GPS_PPS
PB9.Locked=true
PB9.Signal=S_TIM4_CH4
PB9.Stacked=true
PC0.GPIOParameters=GPIO_Label
PC0.GPIO_Label=MBUS_SCL
PC0.Locked=true
PC0.Mode=I2C
PC0.Signal=I2C3_SCL
PC1.GPIOParameters=GPIO_Label
PC1.GPIO_Label=MBUS_SDA
PC1.Locked=true
PC1.Mode=I2C
PC1.Signal=I2C3_SDA
PC10.GPIOParameters=GPIO_Label
PC10.GPIO_Label=SDIO_D2
PC10.Mode=SD_4_bits_Wide_bus
PC10.Signal=SDMMC1_D2
PC11.GPIOParameters=GPIO_Label
PC11.GPIO_Label=SDIO_D3
PC11.Mode=SD_4_bits_Wide_bus
PC11.Signal=SDMMC1_D3
PC12.GPIOParameters=GPIO_Label
PC12.GPIO_Label=SDIO_CLK
PC12.Mode=SD_4_bits_Wide_bus
PC12.Signal=SDMMC1_CK
PC13.GPIOParameters=GPIO_Label
PC13.GPIO_Label=GPS_RST
PC13.Locked=true
PC13.Signal=GPIO_Output
PC14-OSC32_IN\ (PC14).GPIOParameters=GPIO_Label
PC14-OSC32_IN\ (PC14).GPIO_Label=OSC_32K_IN
PC14-OSC32_IN\ (PC14).Mode=LSE-External-Oscillator
PC14-OSC32_IN\ (PC14).Signal=RCC_OSC32_IN
PC15-OSC32_OUT\ (PC15).GPIOParameters=GPIO_Label
PC15-OSC32_OUT\ (PC15).GPIO_Label=OSC_32K_OUT
PC15-OSC32_OUT\ (PC15).Mode=LSE-External-Oscillator
PC15-OSC32_OUT\ (PC15).Signal=RCC_OSC32_OUT
PC2.GPIOParameters=GPIO_Label
PC2.GPIO_Label=MIC_CCLK1
PC2.Locked=true
PC2.Mode=MOD_MDF_CCK1
PC2.Signal=MDF1_CCK1
PC3.GPIOParameters=GPIO_Label
PC3.GPIO_Label=MBUS_MOSI
PC3.Mode=Full_Duplex_Master
PC3.Signal=SPI2_MOSI
PC6.GPIOParameters=GPIO_Label
PC6.GPIO_Label=SYS_RF_GREEN
PC6.Locked=true
PC6.Signal=GPIO_Output
PC7.GPIOParameters=GPIO_Label
PC7.GPIO_Label=SYS_RF_RED
PC7.Locked=true
PC7.Signal=GPIO_Output
PC8.GPIOParameters=GPIO_Label
PC8.GPIO_Label=SDIO_D0
PC8.Mode=SD_4_bits_Wide_bus
PC8.Signal=SDMMC1_D0
PC9.GPIOParameters=GPIO_Label
PC9.GPIO_Label=SDIO_D1
PC9.Mode=SD_4_bits_Wide_bus
PC9.Signal=SDMMC1_D1
PD0.GPIOParameters=GPIO_Label
PD0.GPIO_Label=SENS_I2C_SDA
PD0.Mode=I2C
PD0.Signal=I2C5_SDA
PD1.GPIOParameters=GPIO_Label
PD1.GPIO_Label=SENS_I2C_SCL
PD1.Mode=I2C
PD1.Signal=I2C5_SCL
PD12.Locked=true
PD12.Signal=ADC4_IN16
PD13.GPIOParameters=GPIO_Label
PD13.GPIO_Label=EXT_I2C_SDA
PD13.Locked=true
PD13.Mode=I2C
PD13.Signal=I2C4_SDA
PD14.GPIOParameters=GPIO_Label
PD14.GPIO_Label=SYS_GPS_GREEN
PD14.Locked=true
PD14.Signal=GPIO_Output
PD15.GPIOParameters=GPIO_Label
PD15.GPIO_Label=SYS_GPS_RED
PD15.Locked=true
PD15.Signal=GPIO_Output
PD2.GPIOParameters=GPIO_Label
PD2.GPIO_Label=SDIO_CMD
PD2.Mode=SD_4_bits_Wide_bus
PD2.Signal=SDMMC1_CMD
PD3.GPIOParameters=GPIO_Label
PD3.GPIO_Label=MIC_SD0
PD3.Locked=true
PD3.Mode=MOD_MDF_SITF0_CCK0
PD3.Signal=MDF1_SDI0
PD4.GPIOParameters=GPIO_Label
PD4.GPIO_Label=SD_SW
PD4.Locked=true
PD4.Signal=GPIO_Output
PD6.GPIOParameters=GPIO_Label
PD6.GPIO_Label=MIC_SD1
PD6.Mode=MOD_MDF_SITF1_CCK1
PD6.Signal=MDF1_SDI1
PD8.GPIOParameters=GPIO_Label
PD8.GPIO_Label=MBUS_TX_STM_TX
PD8.Locked=true
PD8.Mode=Asynchronous
PD8.Signal=USART3_TX
PE0.GPIOParameters=GPIO_Label
PE0.GPIO_Label=SD_PWR
PE0.Locked=true
PE0.Signal=GPIO_Output
PE10.GPIOParameters=GPIO_Label
PE10.GPIO_Label=RF_BUSY
PE10.Locked=true
PE10.Signal=GPIO_Input
PE11.GPIOParameters=GPIO_Label
PE11.GPIO_Label=RF_NRST
PE11.Locked=true
PE11.Signal=GPIO_Output
PE12.GPIOParameters=GPIO_Label
PE12.GPIO_Label=RF_IRQ
PE12.Locked=true
PE12.Signal=GPXTI12
PE13.GPIOParameters=GPIO_Label
PE13.GPIO_Label=RF_SCK
PE13.Mode=Full_Duplex_Master
PE13.Signal=SPI1_SCK
PE14.GPIOParameters=GPIO_Label
PE14.GPIO_Label=RF_MISO
PE14.Mode=Full_Duplex_Master
PE14.Signal=SPI1_MISO
PE15.GPIOParameters=GPIO_Label
PE15.GPIO_Label=RF_MOSI
PE15.Mode=Full_Duplex_Master
PE15.Signal=SPI1_MOSI
PE2.GPIOParameters=GPIO_Label
PE2.GPIO_Label=SW_USER
PE2.Locked=true
PE2.Signal=GPIO_Output
PE3.GPIOParameters=GPIO_Label
PE3.GPIO_Label=GPS_EN
PE3.Locked=true
PE3.Signal=GPIO_Output
PE4.GPIOParameters=GPIO_Label
PE4.GPIO_Label=MIC_SD3
PE4.Mode=MOD_MDF_SITF3_CCK1
PE4.Signal=MDF1_SDI3
PE5.GPIOParameters=GPIO_Label
PE5.GPIO_Label=MBUS_CS
PE5.Locked=true
PE5.Signal=GPIO_Output
PE6.GPIOParameters=GPIO_Label
PE6.GPIO_Label=MBUS_RST
PE6.Locked=true
PE6.Signal=GPIO_Output
PE7.GPIOParameters=GPIO_Label
PE7.GPIO_Label=MIC_SD2
PE7.Mode=MOD_MDF_SITF2_CCK1
PE7.Signal=MDF1_SDI2
PE8.GPIOParameters=GPIO_Label
PE8.GPIO_Label=RF_CS
PE8.Locked=true
PE8.Signal=GPIO_Output
PH0-OSC_IN\ (PH0).GPIOParameters=GPIO_Label
PH0-OSC_IN\ (PH0).GPIO_Label=HSE_OSC_IN
PH0-OSC_IN\ (PH0).Mode=HSE-External-Oscillator
PH0-OSC_IN\ (PH0).Signal=RCC_OSC_IN
PH1-OSC_OUT\ (PH1).GPIOParameters=GPIO_Label
PH1-OSC_OUT\ (PH1).GPIO_Label=HE_OSC_OUT
PH1-OSC_OUT\ (PH1).Mode=HSE-External-Oscillator
PH1-OSC_OUT\ (PH1).Signal=RCC_OSC_OUT
PH3-BOOT0.GPIOParameters=GPIO_Label
PH3-BOOT0.GPIO_Label=BOOT0
PH3-BOOT0.Locked=true
PH3-BOOT0.Signal=GPIO_Input
PWR.IPParameters=PowerMode
PWR.PowerMode=PWR_SMPS_SUPPLY
PinOutPanel.RotationAngle=0
ProjectManager.AskForMigrate=true
ProjectManager.BackupPrevious=false
ProjectManager.CompilerOptimize=6
ProjectManager.ComputerToolchain=false
ProjectManager.CoupleFile=false
ProjectManager.CustomerFirmwarePackage=
ProjectManager.DefaultFWLocation=true
ProjectManager.DeletePrevious=true
ProjectManager.DeviceId=STM32U5G7VJTxQ
ProjectManager.FirmwarePackage=STM32Cube FW_U5 V1.6.0
ProjectManager.FreePins=false
ProjectManager.HalAssertFull=false
ProjectManager.HeapSize=0x200
ProjectManager.KeepUserCode=true
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

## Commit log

2026-05-07 Updated fab
    [QUICK_TECK.csv, Sheet2.kicad_sch, raylar_v1_00-B_Courtyard.gbr, raylar_v1_00-B_Mask.gbs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]
2026-05-13 Updated readme, magic scripts for exporting schematic and board renders
    [raylar_v1_00-B_Courtyard.gbr, raylar_v1_00-B_Mask.gbs, raylar_v1_00-B_Paste.gbp, raylar_v1_00-B_Silkscreen.gbo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]
